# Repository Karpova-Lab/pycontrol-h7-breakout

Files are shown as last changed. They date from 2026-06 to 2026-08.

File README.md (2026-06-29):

> !!! WARNING !!! This is a work in progress. Please see the [discussion](https://github.com/orgs/pyControl/discussions/171) to see updates and provide feedback.
# pyControl H7 Breakout
A pyControl breakout board using an [STM32H743VIT6](https://www.digikey.com/short/7n8h83wr) microcontroller.

- 480 MHz Cortex-M7, 800 KB SRAM, 32 MB QSPI flash
- 10 pyControl RJ45 behavior ports with ESD protection on all DIO_A, DIO_B, and DIO_C pins
- 4 BNC connectors
- 1 [QWIIC](https://www.sparkfun.com/qwiic) / [Stemma-QT](https://learn.adafruit.com/introducing-adafruit-stemma-qt/what-is-stemma-qt) / [Modulino](https://store.arduino.cc/collections/modulino) connector
- 16 position [terminal block](https://www.digikey.com/en/products/detail/phoenix-contact/1803413/260588) that pairs with a [screw terminal plug](https://www.digikey.com/en/products/detail/phoenix-contact/1803714/260543) and exposes 2 extra POW driver pins, 8 extra digital I/O pins, 5V, 12V and 4 grounds
- USB type C connector with ESD protection
- On/off switch, 4 user buttons, reset button, and a DFU button for bootloader access
- Power indicator LED, 4 user controllable LEDs (red, yellow, green and blue)
- 2 piece bent sheet metal case
- Mounting hole spacing compatible with [DIN adapters](https://www.digikey.com/short/h7977mfv) that securely mount onto [DIN rail](https://www.digikey.com/en/products/filter/hardware-fasteners-accessories/580?s=N4IgjCBcpgHAzFUBjKAzAhgGwM4FMAaEAeygG0QAWMeWSgThAF0iAHAFyhAGV2AnAJYA7AOYgAvkQC0AJiQhUkfgFdCJciACszcZJBzIFACIBJAHIACPhgFYQRU5eu2dQA)

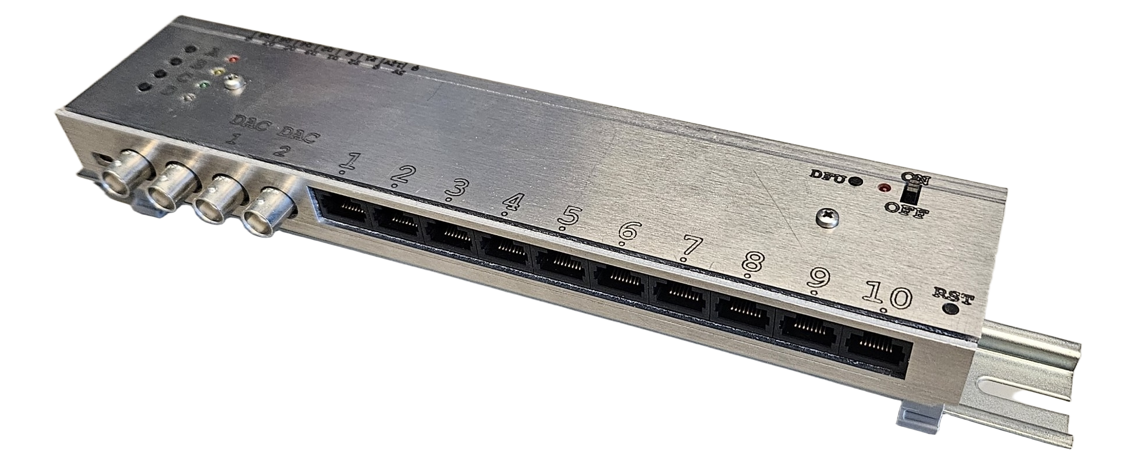
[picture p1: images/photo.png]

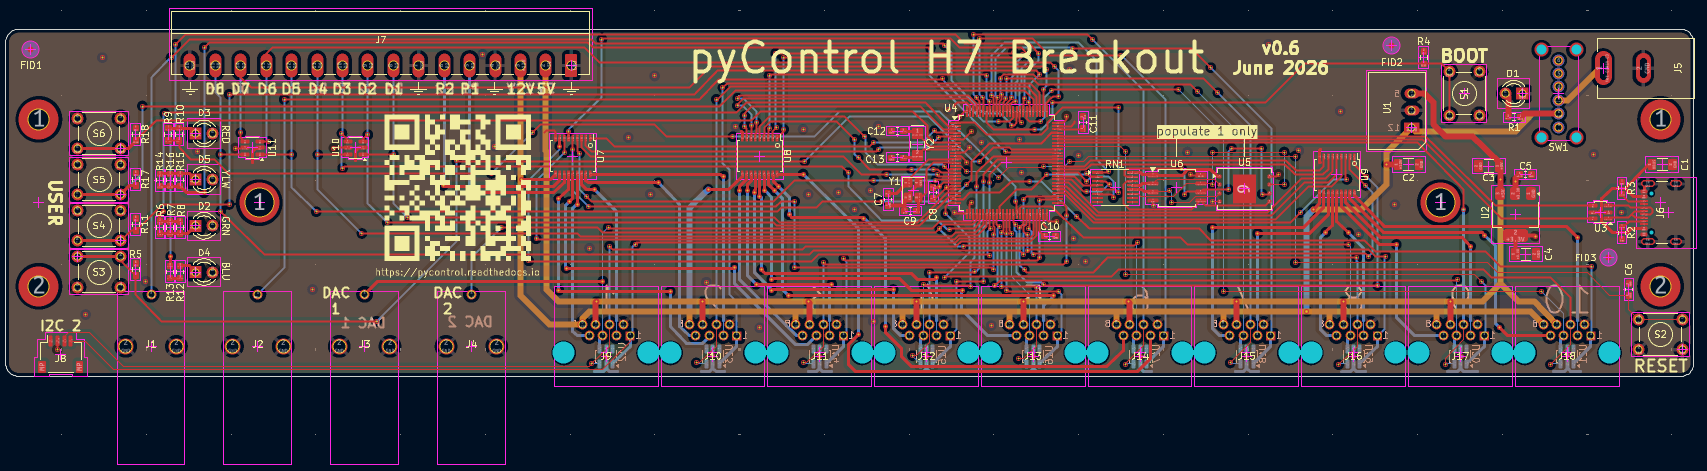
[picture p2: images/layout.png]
layout

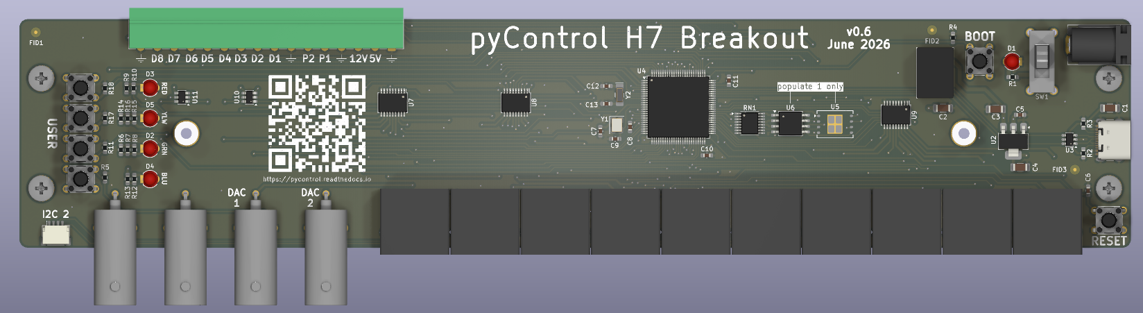
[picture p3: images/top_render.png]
top render

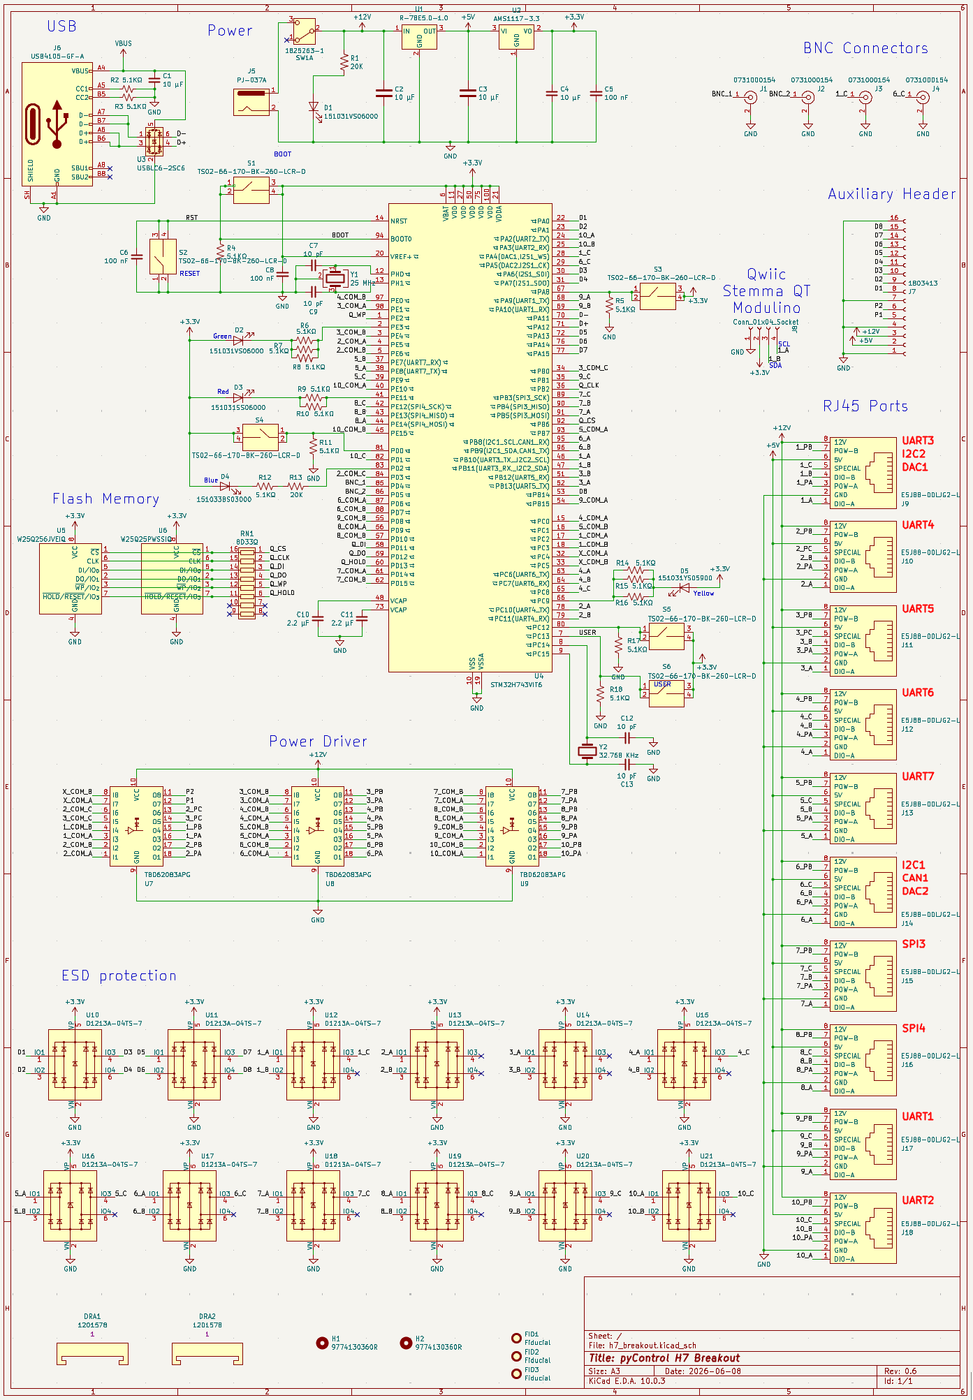
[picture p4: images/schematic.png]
schematic


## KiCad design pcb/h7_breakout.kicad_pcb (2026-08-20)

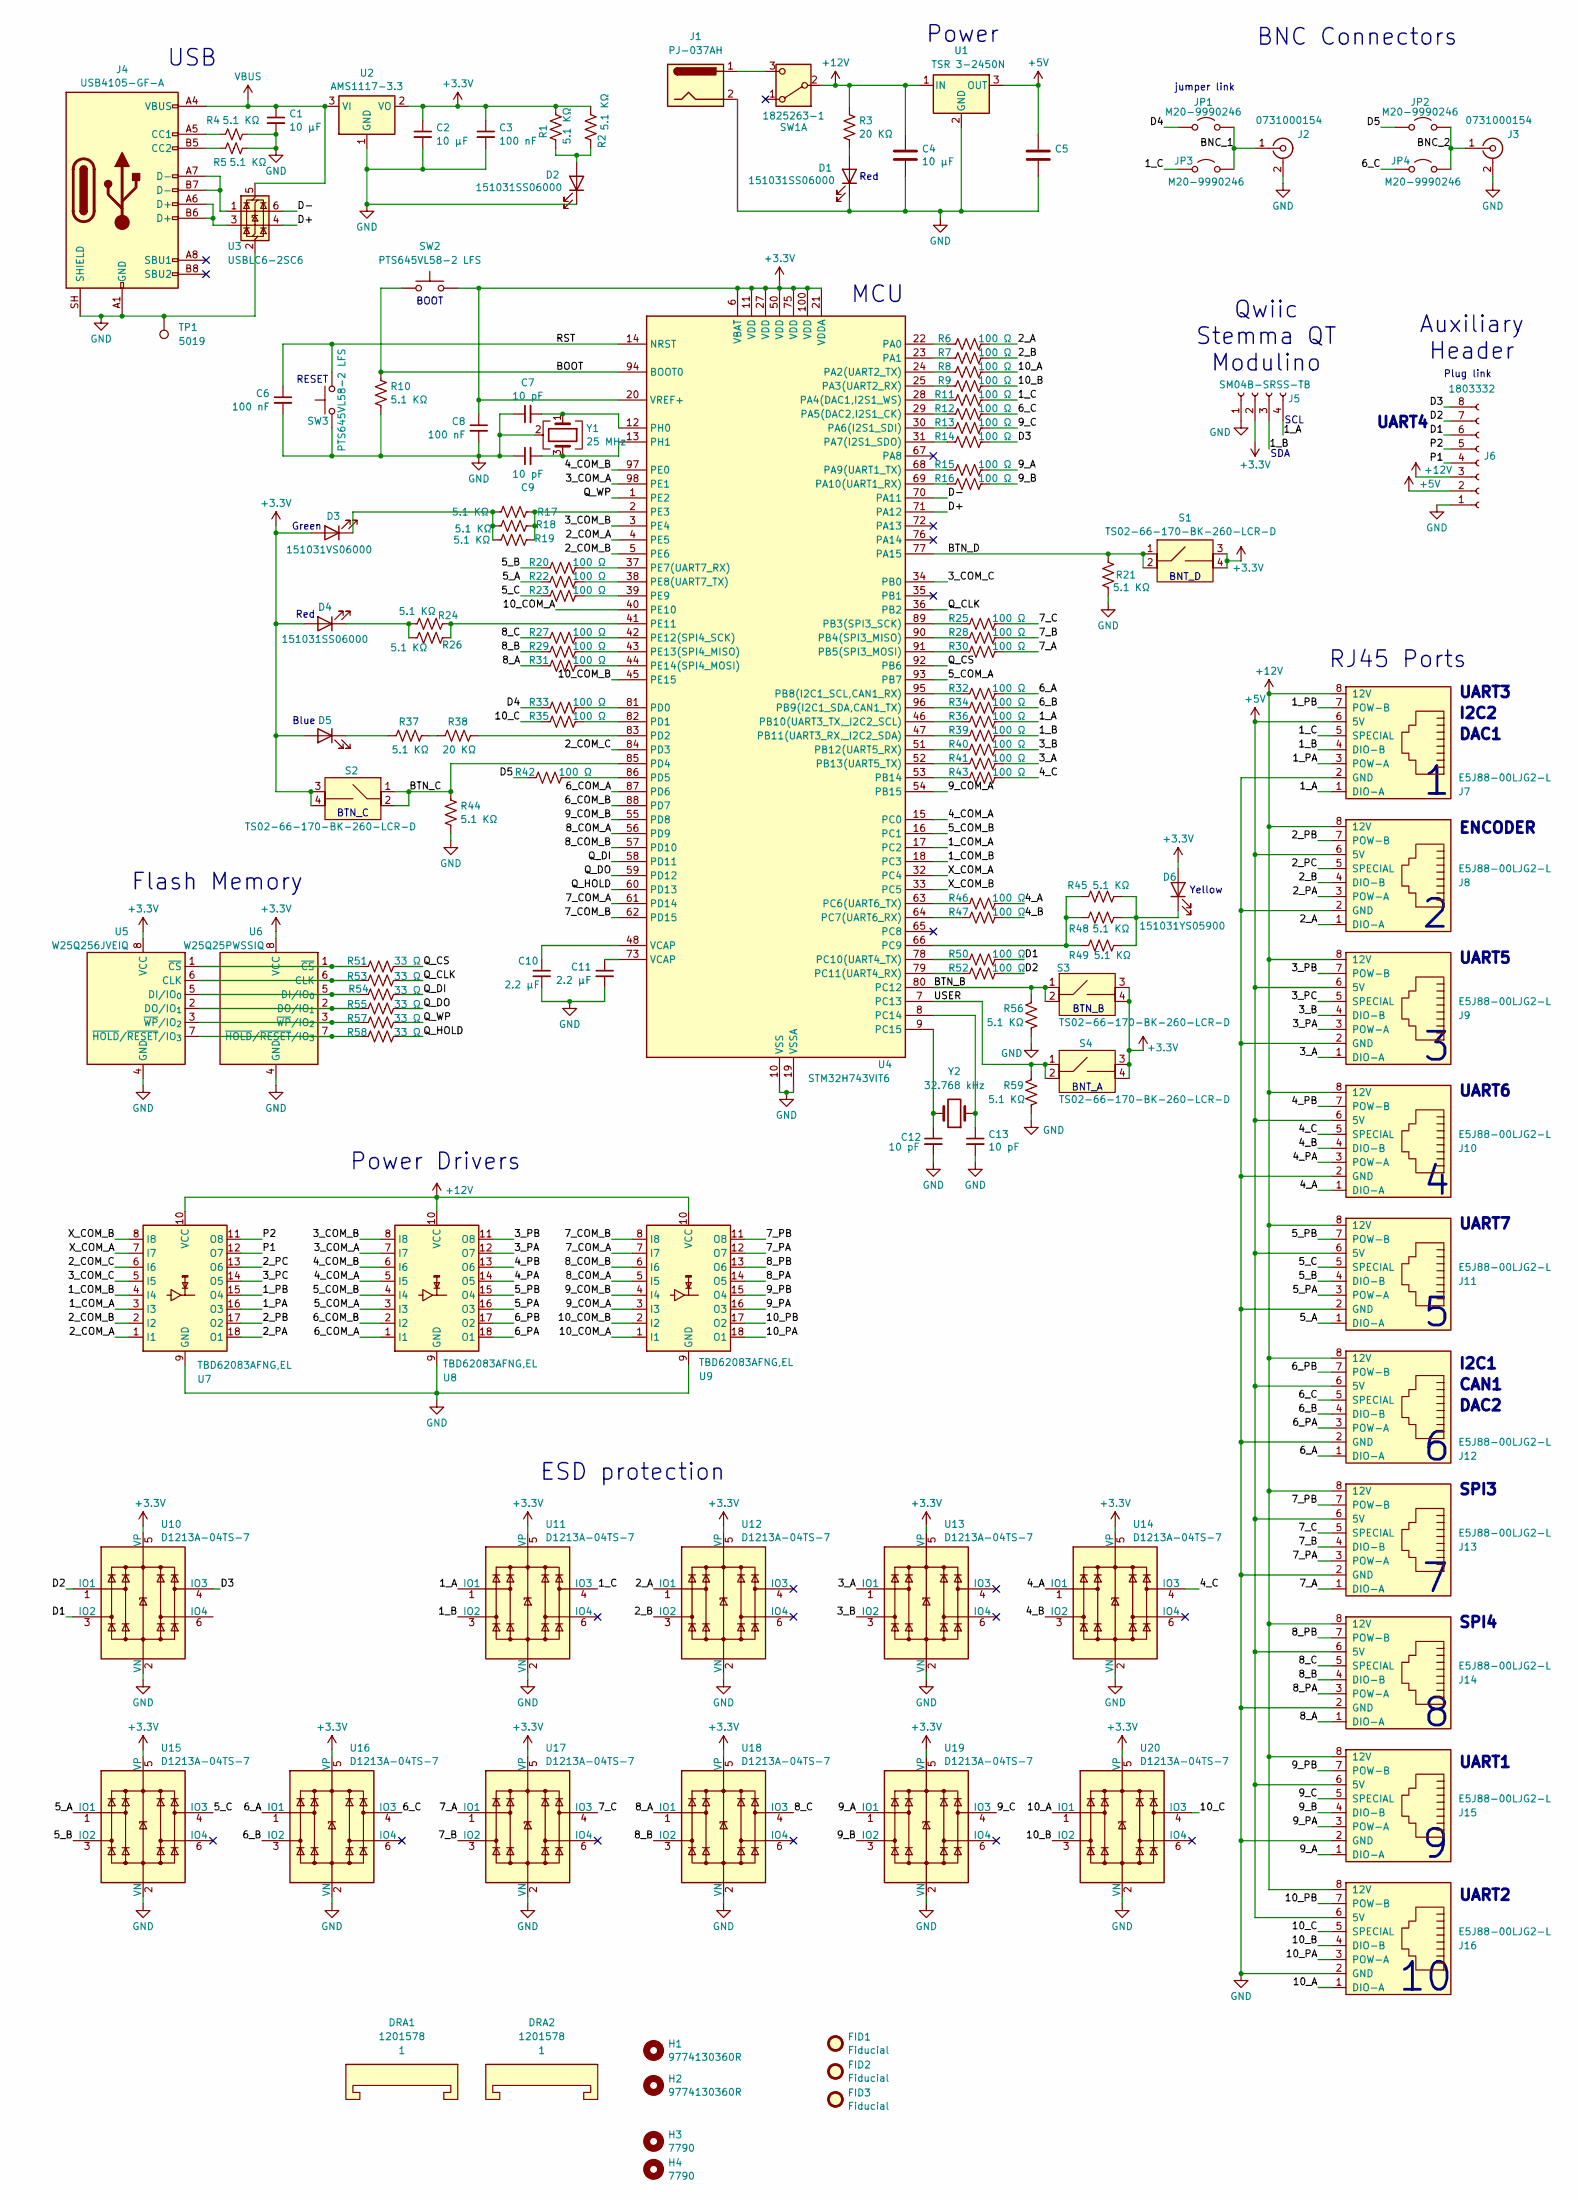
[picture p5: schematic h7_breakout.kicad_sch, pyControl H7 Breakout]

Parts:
C1, C2, C4, C5: 10 µF; C_1206_3216Metric_Pad1.33x1.80mm_HandSolder
C3, C6, C8: 100 nF; C_0603_1608Metric_Pad1.08x0.95mm_HandSolder
C7, C9, C12, C13: 10 pF; C_0603_1608Metric_Pad1.08x0.95mm_HandSolder
C10, C11: 2.2 µF; C_0603_1608Metric_Pad1.08x0.95mm_HandSolder
D1, D2, D4: 151031SS06000; LED_D3.0mm
D3: 151031VS06000; LED_D3.0mm
D5: 151033BS03000; LED_D3.0mm
D6: 151031YS05900; LED_D3.0mm
DRA1, DRA2: 1201578; DIN_Clip
FID1, FID2, FID3: Fiducial; Fiducial_0.75mm_Mask2.25mm
H1, H2: 9774130360R; standoff_nut
H3, H4: 7790; RA_screw_mount
J1: PJ-037AH; DC_Jack
J2, J3: 0731000154; BNC RA Jack
J4: USB4105-GF-A; USB_C_Receptacle_GCT_USB4105-xx-A_16P_TopMnt_Horizontal
J5: SM04B-SRSS-TB; JST_SH_SM04B-SRSS-TB_1x04-1MP_P1.00mm_Horizontal
J6: 1803332; PhoenixContact_MC_1,5_8-G-3.81_1x08_P3.81mm_Horizontal
J7, J8, J9, J10, J11, J12, J13, J14, J15, J16: E5J88-00LJG2-L; RJ45_THP_tab_on_top
JP1, JP2, JP3, JP4: M20-9990246; PinHeader_1x02_P2.54mm_Vertical
R1, R2, R4, R5, R10, R17, R18, R19, R21, R24, R26, R37, R44, R45, R48, R49, R56, R59: 5.1 KΩ; R_0603_1608Metric_Pad0.98x0.95mm_HandSolder
R3, R38: 20 KΩ; R_0603_1608Metric_Pad0.98x0.95mm_HandSolder
R6, R7, R8, R9, R11, R12, R13, R14, R15, R16, R20, R22, R23, R25, R27, R28, R29, R30, R31, R32, R33, R34, R35, R36, R39, R40, R41, R42, R43, R46, R47, R50, R52: 100 Ω; R_0603_1608Metric_Pad0.98x0.95mm_HandSolder
R51, R53, R54, R55, R57, R58: 33 Ω; R_0603_1608Metric_Pad0.98x0.95mm_HandSolder
S1, S2, S3, S4: TS02-66-170-BK-260-LCR-D; SW_TH_Tactile_TS02-66-170
SW1: 1825263-1; RA toggle
SW2, SW3: PTS645VL58-2 LFS; SW_Tactile_SPST_Angled_PTS645Vx58-2LFS
TP1: 5019; TestPoint_Keystone_5019_Miniature
U1: TSR 3-2450N; Converter_DCDC_traco_3A
U2: AMS1117-3.3; SOT-223-3_TabPin2
U3: USBLC6-2SC6; SOT-23-6; LCSC C7519
U4: STM32H743VIT6; LQFP-100_14x14mm_P0.5mm; LCSC C114409
U5: W25Q256JVEIQ; WSON-8-1EP_8x6mm_P1.27mm_EP3.4x4.3mm; LCSC C97522
U6: W25Q25PWSSIQ; SOIC-8_5.3x5.3mm_P1.27mm
U7, U8, U9: TBD62083AFNG,EL; SSOP-18_4.4x6.5mm_P0.65mm; LCSC C163229
U10, U11, U12, U13, U14, U15, U16, U17, U18, U19, U20: D1213A-04TS-7; SOT-23-6; LCSC C460588
Y1: 25 MHz; crystal_STDCRS2-25M
Y2: 32.768 kHz; Crystal_SMD_EuroQuartz_EQ161-2Pin_3.2x1.5mm_HandSoldering

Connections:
+5V: C5.1, J6.2, J7.6 (5V), J8.6 (5V), J9.6 (5V), J10.6 (5V), J11.6 (5V), J12.6 (5V), J13.6 (5V), J14.6 (5V), J15.6 (5V), J16.6 (5V), U1.3 (OUT)
+12V: C4.1, J6.3, J7.8 (12V), J8.8 (12V), J9.8 (12V), J10.8 (12V), J11.8 (12V), J12.8 (12V), J13.8 (12V), J14.8 (12V), J15.8 (12V), J16.8 (12V), R3.1, SW1.2 (B), U1.1 (IN), U7.10 (VCC), U8.10 (VCC), U9.10 (VCC)
/1_A: J5.4, J7.1 (DIO-A), R36.2, U11.1 (IO1)
/1_B: J5.3, J7.4 (DIO-B), R39.2, U11.3 (IO2)
/1_C: J7.5 (SPECIAL), JP3.1 (A), R11.2, U11.4 (IO3)
/1_COM_A: U4.17 (PC2), U7.3 (I3)
/1_COM_B: U4.18 (PC3), U7.4 (I4)
/1_PA: J7.3 (POW-A), U7.16 (O3)
/1_PB: J7.7 (POW-B), U7.15 (O4)
/2_A: J8.1 (DIO-A), R6.2, U12.1 (IO1)
/2_B: J8.4 (DIO-B), R7.2, U12.3 (IO2)
/2_COM_A: U4.4 (PE5), U7.1 (I1)
/2_COM_B: U4.5 (PE6), U7.2 (I2)
/2_COM_C: U4.84 (PD3), U7.6 (I6)
/2_PA: J8.3 (POW-A), U7.18 (O1)
/2_PB: J8.7 (POW-B), U7.17 (O2)
/2_PC: J8.5 (SPECIAL), U7.13 (O6)
/3_A: J9.1 (DIO-A), R41.2, U13.1 (IO1)
/3_B: J9.4 (DIO-B), R40.2, U13.3 (IO2)
/3_COM_A: U4.98 (PE1), U8.7 (I7)
/3_COM_B: U4.3 (PE4), U8.8 (I8)
/3_COM_C: U4.34 (PB0), U7.5 (I5)
/3_PA: J9.3 (POW-A), U8.12 (O7)
/3_PB: J9.7 (POW-B), U8.11 (O8)
/3_PC: J9.5 (SPECIAL), U7.14 (O5)
/4_A: J10.1 (DIO-A), R46.2, U14.1 (IO1)
/4_B: J10.4 (DIO-B), R47.2, U14.3 (IO2)
/4_C: J10.5 (SPECIAL), R43.2, U14.4 (IO3)
/4_COM_A: U4.15 (PC0), U8.5 (I5)
/4_COM_B: U4.97 (PE0), U8.6 (I6)
/4_PA: J10.3 (POW-A), U8.14 (O5)
/4_PB: J10.7 (POW-B), U8.13 (O6)
/5_A: J11.1 (DIO-A), R22.1, U15.1 (IO1)
/5_B: J11.4 (DIO-B), R20.1, U15.3 (IO2)
/5_C: J11.5 (SPECIAL), R23.1, U15.4 (IO3)
/5_COM_A: U4.93 (PB7), U8.3 (I3)
/5_COM_B: U4.16 (PC1), U8.4 (I4)
/5_PA: J11.3 (POW-A), U8.16 (O3)
/5_PB: J11.7 (POW-B), U8.15 (O4)
/6_A: J12.1 (DIO-A), R32.2, U16.1 (IO1)
/6_B: J12.4 (DIO-B), R34.2, U16.3 (IO2)
/6_C: J12.5 (SPECIAL), JP4.1 (A), R12.2, U16.4 (IO3)
/6_COM_A: U4.87 (PD6), U8.1 (I1)
/6_COM_B: U4.88 (PD7), U8.2 (I2)
/6_PA: J12.3 (POW-A), U8.18 (O1)
/6_PB: J12.7 (POW-B), U8.17 (O2)
/7_A: J13.1 (DIO-A), R30.2, U17.1 (IO1)
/7_B: J13.4 (DIO-B), R28.2, U17.3 (IO2)
/7_C: J13.5 (SPECIAL), R25.2, U17.4 (IO3)
/7_COM_A: U4.61 (PD14), U9.7 (I7)
/7_COM_B: U4.62 (PD15), U9.8 (I8)
/7_PA: J13.3 (POW-A), U9.12 (O7)
/7_PB: J13.7 (POW-B), U9.11 (O8)
/8_A: J14.1 (DIO-A), R31.1, U18.1 (IO1)
/8_B: J14.4 (DIO-B), R29.1, U18.3 (IO2)
/8_C: J14.5 (SPECIAL), R27.1, U18.4 (IO3)
/8_COM_A: U4.56 (PD9), U9.5 (I5)
/8_COM_B: U4.57 (PD10), U9.6 (I6)
/8_PA: J14.3 (POW-A), U9.14 (O5)
/8_PB: J14.7 (POW-B), U9.13 (O6)
/9_A: J15.1 (DIO-A), R15.2, U19.1 (IO1)
/9_B: J15.4 (DIO-B), R16.2, U19.3 (IO2)
/9_C: J15.5 (SPECIAL), R13.2, U19.4 (IO3)
/9_COM_A: U4.54 (PB15), U9.3 (I3)
/9_COM_B: U4.55 (PD8), U9.4 (I4)
/9_PA: J15.3 (POW-A), U9.16 (O3)
/9_PB: J15.7 (POW-B), U9.15 (O4)
/10_A: J16.1 (DIO-A), R8.2, U20.1 (IO1)
/10_B: J16.4 (DIO-B), R9.2, U20.3 (IO2)
/10_C: J16.5 (SPECIAL), R35.1, U20.4 (IO3)
/10_COM_A: U4.40 (PE10), U9.1 (I1)
/10_COM_B: U4.45 (PE15), U9.2 (I2)
/10_PA: J16.3 (POW-A), U9.18 (O1)
/10_PB: J16.7 (POW-B), U9.17 (O2)
/BNC_1: J2.1 (In), JP1.2 (B), JP3.2 (B)
/BNC_2: J3.1 (In), JP2.2 (B), JP4.2 (B)
/BTN_B: R56.2, S3.1 (in1), S3.2 (in2), U4.80 (PC12)
/BTN_C: R44.2, S2.1 (in1), S2.2 (in2), U4.85 (PD4)
/BTN_D: R21.2, S1.1 (in1), S1.2 (in2), U4.77 (PA15)
/D1: J6.6, R50.2, U10.3 (IO2)
/D2: J6.7, R52.2, U10.1 (IO1)
/D3: J6.8, R14.2, U10.4 (IO3)
/D4: JP1.1 (A), R33.1
/D5: JP2.1 (A), R42.1
/D+: U3.4 (I/O2), U4.71 (PA12)
/D-: U3.6 (I/O1), U4.70 (PA11)
/P1: J6.4, U7.12 (O7)
/P2: J6.5, U7.11 (O8)
/Q_CLK: R53.2, U4.36 (PB2)
/Q_CS: R51.2, U4.92 (PB6)
/Q_DI: R54.2, U4.58 (PD11)
/Q_DO: R55.2, U4.59 (PD12)
/Q_HOLD: R58.2, U4.60 (PD13)
/Q_WP: R57.2, U4.1 (PE2)
/USER: R59.2, S4.1 (in1), S4.2 (in2), U4.7 (PC13)
/X_COM_A: U4.32 (PC4), U7.7 (I7)
/X_COM_B: U4.33 (PC5), U7.8 (I8)
unnamed: C10.1, U4.48 (VCAP)
unnamed: C11.1, U4.73 (VCAP)
unnamed: D1.2 (A), R3.2
unnamed: D2.2 (A), R1.2, R2.2
unnamed: D3.1 (K), R17.1, R18.1, R19.1
unnamed: D4.1 (K), R24.1, R26.1
unnamed: D5.1 (K), R37.1
unnamed: D6.1 (K), R45.2, R48.2, R49.2
unnamed: J4.A5 (CC1), R4.1
unnamed: J4.B5 (CC2), R5.2
unnamed: J4.A6 (D+), J4.B6 (D+), U3.3 (I/O2)
unnamed: J4.A7 (D-), J4.B7 (D-), U3.1 (I/O1)
unnamed: R37.2, R38.1
unnamed: J1.1, SW1.3 (C)
unnamed: R6.1, U4.22 (PA0)
unnamed: R7.1, U4.23 (PA1)
unnamed: R8.1, U4.24 (PA2(UART2_TX))
unnamed: R9.1, U4.25 (PA3(UART2_RX))
unnamed: R11.1, U4.28 (PA4(DAC1,I2S1_WS))
unnamed: R12.1, U4.29 (PA5(DAC2,I2S1_CK))
unnamed: R13.1, U4.30 (PA6(I2S1_SDI))
unnamed: R14.1, U4.31 (PA7(I2S1_SDO))
unnamed: R15.1, U4.68 (PA9(UART1_TX))
unnamed: R16.1, U4.69 (PA10(UART1_RX))
unnamed: R25.1, U4.89 (PB3(SPI3_SCK))
unnamed: R28.1, U4.90 (PB4(SPI3_MISO))
unnamed: R30.1, U4.91 (PB5(SPI3_MOSI))
unnamed: R32.1, U4.95 (PB8(I2C1_SCL,CAN1_RX))
unnamed: R34.1, U4.96 (PB9(I2C1_SDA,CAN1_TX))
unnamed: R36.1, U4.46 (PB10(UART3_TX,_I2C2_SCL))
unnamed: R39.1, U4.47 (PB11(UART3_RX,_I2C2_SDA))
unnamed: R40.1, U4.51 (PB12(UART5_RX))
unnamed: R41.1, U4.52 (PB13(UART5_TX))
unnamed: R43.1, U4.53 (PB14)
unnamed: R46.1, U4.63 (PC6(UART6_TX))
unnamed: R47.1, U4.64 (PC7(UART6_RX))
unnamed: R45.1, R48.1, R49.1, U4.66 (PC9)
unnamed: R50.1, U4.78 (PC10(UART4_TX))
unnamed: R52.1, U4.79 (PC11(UART4_RX))
unnamed: C13.1, U4.8 (PC14), Y2.1
unnamed: C12.1, U4.9 (PC15), Y2.2
unnamed: R33.2, U4.81 (PD0)
unnamed: R35.2, U4.82 (PD1)
unnamed: R38.2, U4.83 (PD2)
unnamed: R42.2, U4.86 (PD5)
unnamed: R17.2, R18.2, R19.2, U4.2 (PE3)
unnamed: R20.2, U4.37 (PE7(UART7_RX))
unnamed: R22.2, U4.38 (PE8(UART7_TX))
unnamed: R23.2, U4.39 (PE9)
unnamed: R24.2, R26.2, U4.41 (PE11)
unnamed: R27.2, U4.42 (PE12(SPI4_SCK))
unnamed: R29.2, U4.43 (PE13(SPI4_MISO))
unnamed: R31.2, U4.44 (PE14(SPI4_MOSI))
unnamed: C7.2, U4.12 (PH0), Y1.1
unnamed: C9.2, U4.13 (PH1), Y1.3
unnamed: R53.1, U5.6 (CLK), U6.6 (CLK)
unnamed: R54.1, U5.5 (DI/IO_{0}), U6.5 (DI/IO_{0})
unnamed: R55.1, U5.2 (DO/IO_{1}), U6.2 (DO/IO_{1})
unnamed: R51.1, U5.1 (~CS), U6.1 (~CS)
unnamed: R58.1, U5.7 (~HOLD/~RESET/IO_{3}), U6.7 (~HOLD/~RESET/IO_{3})
unnamed: R57.1, U5.3 (~WP/IO_{2}), U6.3 (~WP/IO_{2})
VBUS: C1.1, J4.A4 (VBUS), J4.A9 (VBUS), J4.B4 (VBUS), J4.B9 (VBUS), U2.3 (VI), U3.5 (VBUS)

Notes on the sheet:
SDA
I2C2
UART4
Plug link
jumper link
Power Drivers
Auxiliary Header
ESD protection
ENCODER
BOOT
USB
Red
SPI4
Qwiic Stemma QT Modulino
I2C1
BTN_B
RJ45 Ports
BNT_D
SCL
Flash Memory
BNT_A
DAC1
UART6
SPI3
UART1
UART3
DAC2
Blue
UART7
UART2
RESET
Green
BNC Connectors
UART5
Power
Yellow
CAN1
BTN_C
MCU

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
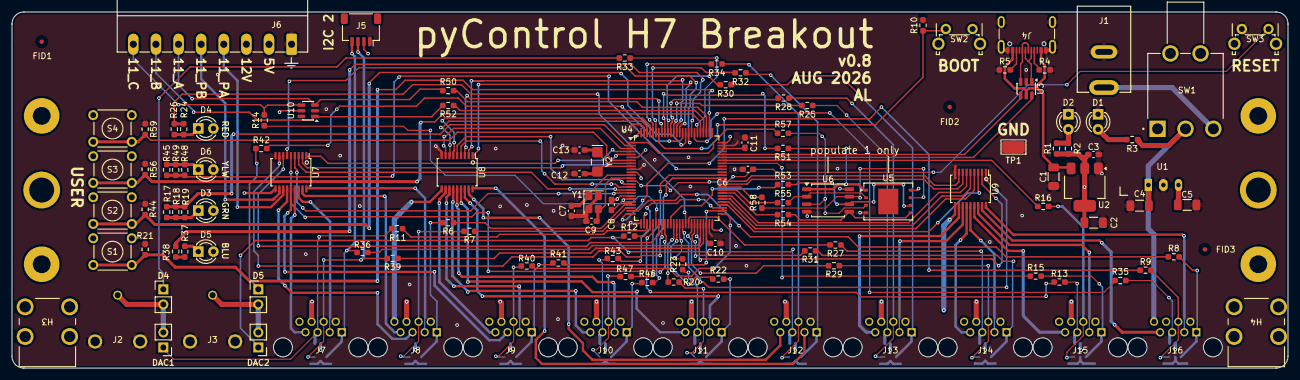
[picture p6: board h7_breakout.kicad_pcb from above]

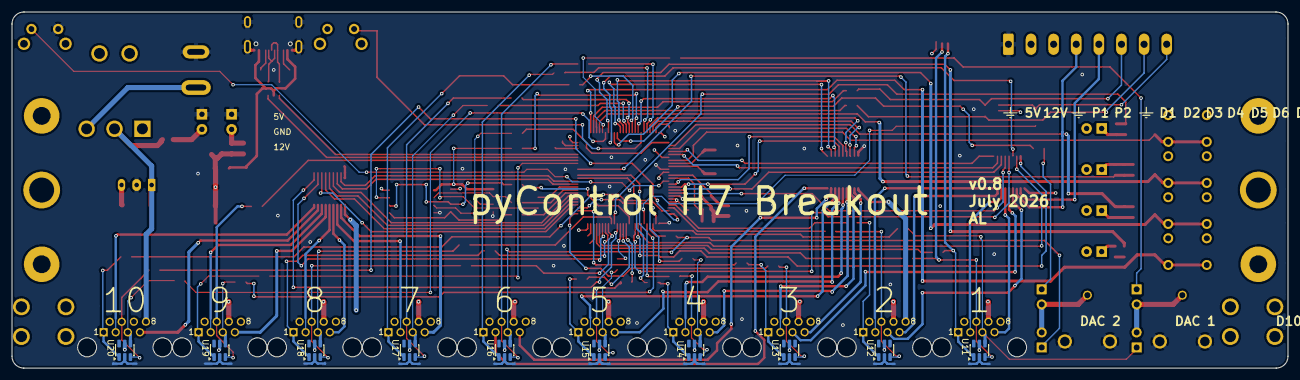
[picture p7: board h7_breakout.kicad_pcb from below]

Board: 4 copper layers, 215.0 x 60.0 mm, 137 parts (12 on the bottom side), 163 nets.

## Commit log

2026-03-12 PCB v0.2
    [h7_breakout.kicad_pcb, h7_breakout.kicad_sch]
2026-03-26 PCB v0.3
    don't short the power supply with the on/off switch 🤦
    flipped UART4 pins. TX(4_A)/RX(4_B) was PC11(79)/PC10(78), now PC10(78)/PC11(79)
    connect Vref to 3.3V so DAC works
    change RGB LEDs to 10k
    [h7_breakout.kicad_pcb, h7_breakout.kicad_sch]
2026-04-16 PCB v0.4
    - was 2 layer, now 4 layer board
    - was USB type B, now USB type C connector
    - was SMA coaxial connectors, now BNC
    - was 12 ports, now 10 ports
    - added POW_C pins to 2 of the ports
    - added8 extra GPIOs, 2 POW pins, and 5V/12V/GND rails on 16 pin terminal block
    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
    [h7_breakout.kicad_pcb, h7_breakout.kicad_sch]
2026-05-16 PCB v0.5
    - connect USB-C shield ground
    - connect A6/B6 and A7/B7 on USB-C
    - connect C13 to ground
    - use 5.1K resistors for everything
    - make DC-DC converter pads smaller
    - added QR code
    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
    [h7_breakout.kicad_pcb, h7_breakout.kicad_sch]
2026-06-08 PCB v0.6
    [h7_breakout.kicad_pcb, h7_breakout.kicad_sch]
